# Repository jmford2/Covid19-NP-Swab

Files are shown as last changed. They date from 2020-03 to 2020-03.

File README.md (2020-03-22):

*Last updated: March 22, 2020 08:00 ET*

# Making NP swabs

As clinical laboratories around the world have begun testing for Covid-19, we have encountered a new crisis: a shortage of the swabs required to obtain the necessary sample. These are called nasopharyngeal swabs, or NP swabs for short.

**The goal of this repository is sharing [methods](#design), [testing procedures](#testing), and [results](#results) required to manufacture NP swabs locally/everywhere at volumes of thousands per day, until standard manufacturers can make and deliver more.**

Because the crisis is **now,** the goal is to re-create versions of the swabs already in use (as opposed to creating better/fundamentally different redesigns).

The files in this repo contain some information to get started. **This includes .stl files that you can modify/print (see [design_files](design_files/) above).**

If anyone has any questions, please reach out to any of the contributors here or to Dr. Ramy Arnaout, MD, DPhil, at rarnaout@bidmc.harvard.edu.

Anything you find here is free for use for all.

### High-level summary, March 21:

We are pursuing three main approaches:
- 3D printing [shafts](#design) and [gluing](#adhesive) [flock](#flock). We have good shaft designs modeled on the images below. Bottlenecks (1) [finding](#adhesive)/[testing](#testing) PCR-compatible glues. (2) High-throughput assembly and packaging. [Results](#results) should start appearing below.

- 3D printing all-in-one swab (meaning printing bristles together with/on shaft). We have promising designs (something like the below; stl/CAD files coming) but need to iterate to get to something usable; bottleneck is materials testing.

- Repurposing existing swabs. We are testing materials.

We will report results as we have them below.

If you want us to test swab materials at BIDMC we are happy to, you can **overnight** them to **Dr. Ramy Arnaout, MD DPhil, 508 Heath Street #2, Chestnut Hill, MA 02467** (note we are setting up dedicated 24/7 receiving at the hospital so this address will change, but your material will still get here). 

For efficiency, we strongly suggest you find local partners either in addition or instead for [testing](#testing) and ask one of [us](#contact) for write access to share your [results](#results) here on the repo.

## Contents

- [Basic description of an NP swab](#design)
- [Requirements](#reqs)
- [Anti-requirements: What's not required](#not-reqs)
- [List of known acceptable swabs](#acceptable-swabs)
- [Manufacturing approaches](#approaches)
- [Flock](#flock)
- [Materials and adhesives](#adhesive)
- [Packaging](#packaging)
- [Testing procedures](#testing)
- [Results](#results)
- [Contact](#contact)

## Basic description of an NP swab

(Click images for larger versions)

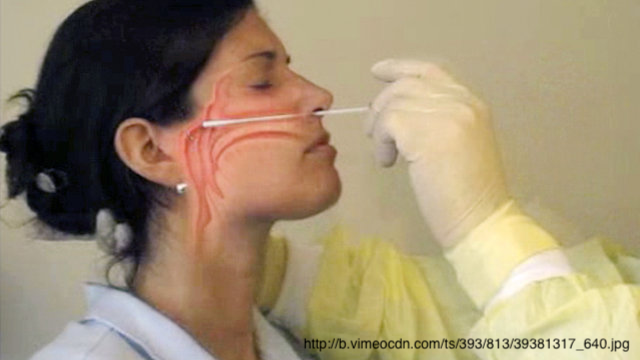
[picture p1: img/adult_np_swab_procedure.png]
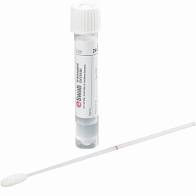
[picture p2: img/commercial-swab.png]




An NP swab is a flexible stick around 15cm in length that goes up your nose to the back of the nasal cavity (see [movie](https://www.youtube.com/watch?v=hXohAo1d6tk&feature=youtu.be&t=40)). It is swept or twirled around to brush or wick up secretions, which carry Covid-19 virus particles. The swab comes out of the nose and goes into a vial that contains fluid ([viral transport medium, VTM](Other_Docs/VTM_IU_recipe.pdf)). The vial gets capped and sent for processing.

There are **two parts**: a bristled **bulb** end (above) and a **shaft**. The bristles in the above are nylon.

The bulb looks like it would be fluffy to the touch but it is not: the bristles are short enough that it feels more like hard foam.

Often the shaft itself has a thin **neck**, for flexibility, and a thicker **handle**. The handle is often **scored**---a weak point in the shaft---where you can break it off so the bristled part stays in the vial; the handle is then thrown away.

**Score at \~7 cm from bulb tip.** The location of the score (distance from the bulb along the handle) must be smaller than the height of the vial you use. For example, for the vials for use with Copan 480C swabs, the breakpoint is 7cm; for [15-](https://www.fishersci.com/shop/products/falcon-15ml-conical-centrifuge-tubes-5/p-193301) or [50-mL](https://www.fishersci.com/shop/products/falcon-50ml-conical-centrifuge-tubes-2/p-193321) conical tubes (of the kind used routinely in biomedical research and sold by many manufacturers), 11 cm will do. It is mildly easier for handling if the score is close to the height of the vial but the requirement is that it is less than the height.

Helpful target measurements:

- Diameter of head with bristles: 3mm
- Diameter of head without bristles: \~2mm
- Diameter of neck: 1mm
- Diameter of handle: 2.5mm
- Length of bulb: 15mm
- Length that will be submerged in [transport medium](#pcr): \~30mm

# Requirements

## Medical requirements

-	**Stiffness, flexibility.** Wand is stiff enough to push to the back of the nasal cavity but flexible enough to get up the nose and will bend when it hits resistance instead of stabbing people (for reference, swabs are a little more flexible than the tiny straws used for coffee, and somewhat similar to the inside tube that holds the ink when you take apart a Bic ballpoint pen). **Swab must not snap off in patient's nose**

-	**Tip.** Ideally, the bulb end is *flocked* (see below): it has lots of tiny bristles perpendicular to the wand (see close-up above). The bristles provide for a high surface-area-to-volume and helps both wick secretions onto the bristle and liberate particles when put in the transport medium. Perpendicularity is a nice-to-have that we believe may improve yield slightly but requires electrostatic deposition; even random orientation of flock should work fine

-	Bristles or collecting substrate (including any adhesive) must be firmly attached and not get left behind in the nasal cavity. Similarly no part of the swab should break off or get left in the nasal cavity

-	[Materials](#adhesive) cannot inhibit [PCR](https://en.wikipedia.org/wiki/Reverse_transcription_polymerase_chain_reaction). This means no wood or cotton (although we believe rayon is OK). Nylon and polypropylene seem to be good choices, but start with medical equipment/grade materials if possible since they should be high quality/pure (some additives can be inihibitors).

-	Wand must break off inside the tube – better to be too short than too long.  Wand could be manually scored to create a weak point. If not, might need scissors at point of care (not ideal)

For more technical requirements, see [Design Constraints](Other_Docs/Design%20Constraints.md)

## Anti-requirements: What's not required

-	Sterility. Not a major concern for most uses; only for immunocompromised (in which case the ability to decontaminate by [autoclaving](https://en.wikipedia.org/wiki/Autoclave) or ethanol or isopropanol bath is needed). The air and the nose are already non-sterile and the PCR assay is specific enough to ignore most contaminants (as long as other Covid-19 contaminated things/people don’t come in contact with it and it doesn’t pick up PCR inhibitors)

-	Labor intensive is ok, to fill short term needs. There are students and researchers out of school and lab who are willing to volunteer to hand-assemble these from inoculation loops, adhesive, and wicking substrate #studentArmy

## List of known acceptable swabs

Model what you make after one of these.

Product numbers are listed. Unless otherwise stated, these are from the [FDA approved list](https://www.fda.gov/medical-devices/emergency-situations-medical-devices/faqs-diagnostic-testing-sars-cov-2) current as of **March 20, 2020**. You can look these up online.

**Copan:** 480C *(2)*, 481C *(1)*, 482C *(1)*, 501CS01, 503CS01, 516CS01, 518CS01, 534CS01

**Puritan:** LA-117 *(1)*, 3317-H, 25-3317-H, 25-3316-U, 25-3316-H, 25-3317-U, 25-3318-U, 25-3318-H, 25-3319-H, 25-3320-U, 25-3320-U EMB 100MM, 25-3320-U EMB 80MM, 25-3320-H and 25-3320-H EMB 80MM

*(1)* Preferred, per FDA

*(2)* Acceptable, per BIDMC

## Manufacturing approaches

**We believe the best use of resources is to be creative around copying the template, not redesigning swabs.**

- 3D print a shaft, and attaching flock material via adhesive

- 3D print a shaft with enough definition---either "nubs" along the surface or bristles---to gather secretion from the nasopharynx.

For more detail on ideas not yet investigated, including repurposing unrelated items like cosmetics applicators, or using other items common in labs, see [Other Approaches](Other_Docs/Repurposing_Approach.md)

### 3D-print shaft + adhesive + swab

- 3D print a wand with the appropriate form factor (e.g. see the picture above and the .stl files)
- dip bulb in adhesive (we are working on appropriate adhesives)
- dip sticky bulb in [flock](#flock)
- shake/blow/rinse off excess flock
- (if needed) dip in 70% ethanol for sterilization

(This is like how you'd solve this problem if you were in elementary school.) Currently we have no proven way to automate the last three steps so we are envisioning a "student army." Better ideas welcome.

### 3D-print entire swab

The ability to print a swab complete with bristles or equivalent saves the steps for requiring adhesive and [flock](#flock). 

Stereolithography 3D printed prototypes by **OPT Industries** look promising (see example bulbs, below---note in this approach the whole swab including bulb is printed at once, on their own DLP/SLA machines); we are testing materials now.
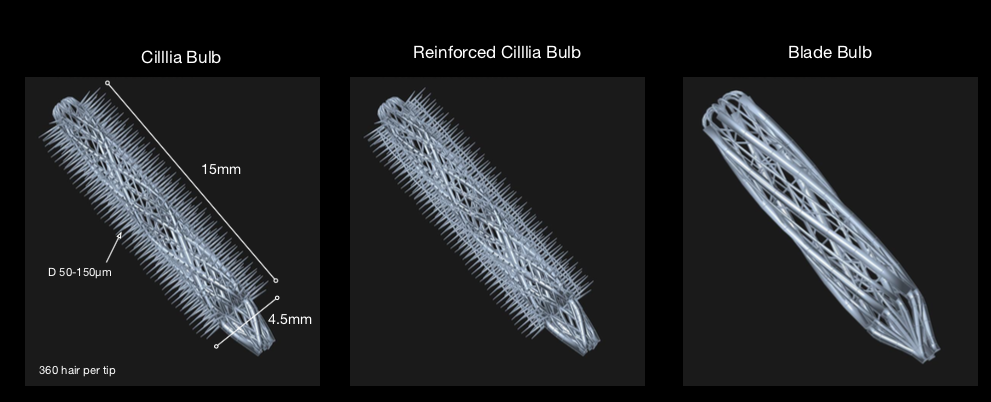
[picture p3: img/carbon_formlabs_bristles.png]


## Flock

"Flock" is the name of the bristle material. It can be ordered from e.g. www.flockit.com as a powder. The below information comes from extremely helpful conversations with them and Celluseude, the manufacturer.

- The nylon flock on the tip of the picture is 3 [denier](https://en.wikipedia.org/wiki/Units_of_textile_measurement#Denier) (3 [dtex](https://en.wikipedia.org/wiki/Units_of_textile_measurement#Denier))

- The flock on the flocked swab above was likely applied using electrostatic deposition: flock coated with something positively charged, shaft coated with adhesive and electrically grounded. We do not need to do this: the previous version of swabs, still widely in use, have matted flock and they work well enough (slightly lower sensitivity but clinically for now we'll take it)

- In general acrylic is used as the adhesive for flock, but be aware that acrylic is a **known PCR inhibitor** (see below). Decision point is rinse a lot to remove loose acrylic vs. just use something safer. Apparently Elmer's has something of the same problem.

- The only colors you should consider for the nylon are black and white, with preference for white. Black has some inorganic compound that is assumed to be PCR-safe; white has titanium inside the fiber but not on the surface so is more likely PCR safe. (White is the purest nylon.) Colored nylons have various ionic or covalent groups on the outside, which are unnecessary complications.

- Rayon is also safe to use

## Shaft

This is the easiest part to 3D-print.

It should be able to be easily broken off, so that only the tip with the patient's nasal secretion is in a specimen container.  Easy break-off may be accomplished via scoring.

## Packaging

As we get closer to having swabs, we will want a solution for packaging. Ideally at least semi-sterile, definitely single-swab packaging.

Possibly will want to fork this process: more sterile for immunocompromised patients, less for others.

Current best thought is to package manually in sterile hoods:

- begin with swabs in ethanol vat/bucket
- spread and cut plastic wrap
- leave under UV light in hood (*1*)
- take swab out of ethanol and place horizontally on strip of plastic to dry
- **When dry,** fold plastic over swab
- packing done

(*1*) UV is not expected to destroy plastic on timescales of under a few hours

Thoughts on throughputting this?

## Materials and adhesives

Adhesives will need to adhere the two substances (printed shaft + flock) and will need to not leave behind anything in the nasal cavity / nasopharynx when used.

Some materials and adhesives inhibit PCR (see [testing protocol](#pcr) below). See the [Kodzius 2012](Other_Docs/kodzius2012.pdf) and [forensicGEM's work](Other_Docs/forensicGEM_Tissue_AppNote_TapeInhibition.pdf) for details.

From those files:

### Safe materials (any red bar above \~50 in [Kodzius Fig. 3](Other_Docs/kodzius2012.pdf)): (*1*)
- polypropylene
- PTFE
- PDMS
- SiO2 quartz
- Pyrex glass
- Soda-lime glass
- NOA68

### Unsafe materials:
- PMMA
- Silicon
- SiO2 5600A
- ITO glass
- SU-8
- NOA61

### Unknown:
- metals including steel and aluminum (in principle these stick to polymerase, but the effect size depends on the form factor so we don't know yet)
- polycryl resin (we believe the monomers are not PCR safe, but if cured and washed could be ok; we will test)

### Safe adhesives (from Kodzius Fig. 3 and from forensicGEM document Fig. 1):
- Wax (Tm 80C)
- the glue used in Scotch Magic Tape 810
- the glue used in Scotch Crystal Clear Tape
- the glue used in Scotch Mailing Tape
- the glue used in Scotch Storage Freezer Tape
- the glue used in Scotch Transparent Tape 550
- the glue used in Sellotape Brown Packaging Tape
- the glue used in Applied Biosystems MicroSeal Adhesive Film

### Unsafe adhesives:
- Wax (Tm <80C)
- Epoxy glue
- Acrylic glue
- the glue used in Scotch Masking Tape (made in Canada or Taiwan)
- the glue used in Scotch Removable Magic Tape 811
- the glue used in Sellotape Diamond Ultra Clear
- the glue used in Sellotape Invisible Permanent Write-on
- the glue used in Sellotape Cellulose Easy-Tear Tape
- the glue used in Sellotape Double-Sided Tape
- the glue used in 3M PostIt notes

(*1*) Some materials can in principle be used as adhesives, e.g. PDMS

## Testing procedures

We propose/are using a three-step testing procedure:

- expert review
- sufficient collection of material
- PCR compatibility

### Expert review

There is no substitute for having a health professional who actively uses NP swabs evaluate your prototype. If such an expert says it "looks good," that is enough to pass this test (see [Results](#results) below)

Two frequently-asked questions are re: length and flexibility. For length, our current recommendation is 15cm. For flexibility: if you have a [swab to compare to](#acceptable-swabs), that is the best way to guage flexibility. If not: your swab should as flexible as the inside part of a standard Bic ball-point pen (the tube that contains the actual ink, when you take the pen apart).

### Sufficient collection of material

For collection of material:

- swirl against the inside of your cheek (make sure the swab is clean first)
- rub on a slide
- perform a [Gram stain](https://en.wikipedia.org/wiki/Gram_stain)
- visualize under a microscope
- take picture through ocular
- compare picture to control we made using an actual NP swab (to be posted soon)

The viral particles we are looking to collect are smaller than bacteria, but if you collect a fair number of bacteria, that is considered Ok for now (ask a microbiologist or microbiology tech, and we will provide a picture of what we think is acceptable when we can).

### PCR compatibility

It is essential to confirm that nothing in the final product (material ± adhesive) inhibits RT-PCR, on which current tests are based (details of the reagents differ somewhat from assay to assay; we will post). A testing protocol is as follows. Note because this has a substantial incubation time, **it is a good idea to start testing materials before prototypes are done, if possible.**

- incubate bulb in 3mL Viral Transport Medium (VTM; [recipe courtesy IU](Other_Docs/VTM_IU_recipe.pdf)) overnight (12 hr)
- spike the VTM with positive control (*1*)
- aliquot 700µl for testing
- run RT-PCR (*2*) (*3*)

(*1*) If you are working with clinical labs who have the bandwidth, they can use inactivated Covid-19 particles that are used clinically as the positive control any virus. If not, and you are/have access to colleagues in a virology lab working with encapsulated virus, that can be used. If not, then any mRNA.

(*2*) Many protocols and reagents are proprietary, but many hospitals have developed their own laboratory-developed tests (LDTs) that may have made their protocols publicly available. If you find and [forward](#contact) we will post.

(*3*) An RNA extraction step [may not be required](https://www.biorxiv.org/content/10.1101/2020.03.20.001008v1)

See also [this FDA page](https://www.fda.gov/medical-devices/emergency-situations-medical-devices/faqs-diagnostic-testing-sars-cov-2) for speific testing details.

## Results

As materials and designs (including existing swabs) get tested, we will record results here. Please organize entries into the following fields. We plan to turn into a (sortable) table, but don't wait for that: just upload entries (separating each entry by line breaks). Please **copy** the below for each entry (i.e., don't overwrite it). If you need help [contact us](#contact).

___

### ENTRY TEMPLATE

#### Identifier
This is a unique identifier, ideally including the source's name

#### Date of test

#### Test site
E.g., BIDMC

#### Picture
Please take a high-resolution picture of the **entire** item provided.

#### Material
Please describe all (known) materials in the bulb head, including plastic, any adhesive, and any flock

#### Process
Please include a brief description of the design process that an expert would understand well enough to reproduce. For repurposed swabs, write "commercial."

#### Creator (contact info and company)
How to contact the creator for questions/further development

#### Link to stl and cad files
Please send .stl and CAD files, which we will post.

#### Test 1: NP swab user evaluation (eg an ID doc), with comments
If passes, write "Pass". If fails, write "Fail" and give a brief reason why. Should be filled out by someone who has experience actually using NP swabs in a clinical context. Please leave the name of this person.

#### Test 2: Collection test
If a Gram stain of the (inner) cheek made from the swab shows material broadly consistent with our control, then write "Pass". If not, "Fail" and give reason (too abrasive, did not pick up material, etc.)

#### Test 3: PCR compatibility (and which protocol used)
As above, "Pass" vs. "Fail". Please indicate the protocol used. You can post the protocol in the Testing/ directory, and link to it here

___

## Contact us

We want to emphasize this is a **group effort** with literally scores of people working on this right now; if you're reading this, you're probably one of them. If you have something to contribute, please contact Dr. Ramy Arnaout, MD, DPhil, at rarnaout@bidmc.harvard.edu.

Note there's also now a [Slack channel](https://join.slack.com/t/rapidmanufact-iop4498/shared_invite/zt-cykndes6-XtxzG~8bkji64M3wTVWiOw).

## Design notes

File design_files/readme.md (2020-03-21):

# Please upload and download models here

## Abiogenix Models
- Goutam Reddy (greddy@abiogenix.com)
- Fusion 360 links to CAD models

1) nasopharyngeal swab nubs V1:  https://a360.co/2Qyh2GE
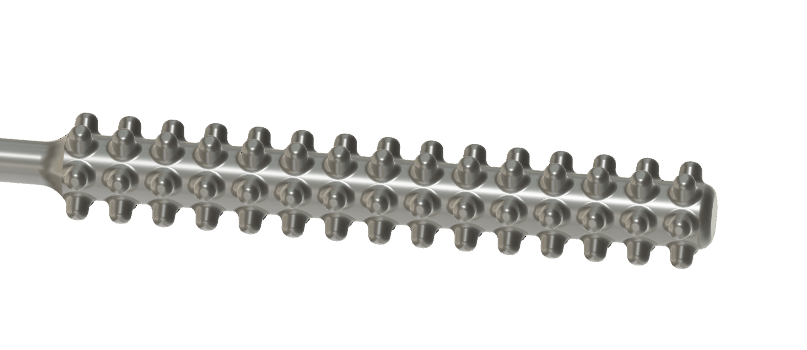
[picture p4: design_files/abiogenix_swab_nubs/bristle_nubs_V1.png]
   - 
   - bristle with 6x15 0.7mm dia raised nubs,
   - bristle surface area 129 mm^2
   - need to fix shaft so max-stress point is at snap-off point, not on bristle shaft
    
2) nasopharyngeal swab round V1:  https://a360.co/2wpGHui
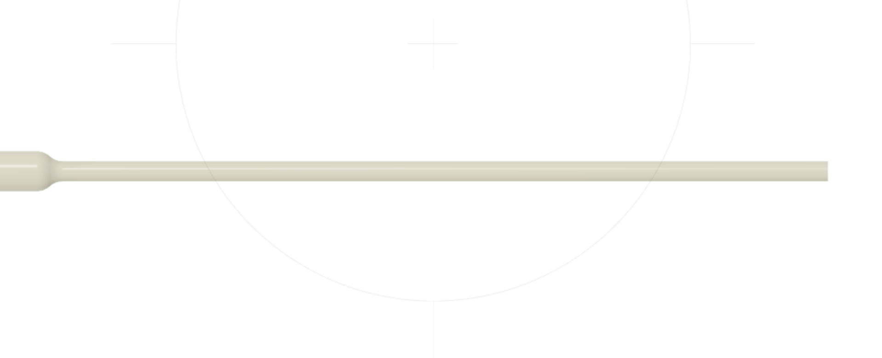
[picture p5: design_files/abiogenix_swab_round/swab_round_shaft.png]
   - 
   - featureless bristle: 1.25mm diameter shaft
   - bristle surface area: 61 mm^2
   - LESS SURFACE AREA BUT CAN BE USED TO ATTACH EXTERNAL BRISTLE OR COATING
   
3) nasopharyngeal swab nubs holes V1: https://a360.co/2U5CzbK
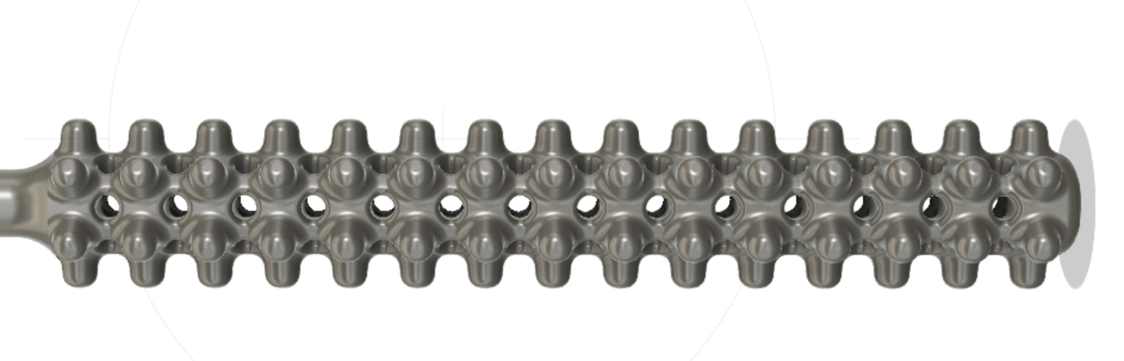
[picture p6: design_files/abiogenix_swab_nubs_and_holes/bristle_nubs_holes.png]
   - 
   - bristle with 6x15 0.7mm dia raised nubs, and 0.35mm dia holes
   - bristle surface area: 167 mm^2
   - PREFER NOT TO USE MODELS WITH HOLES INSIDE TO REDUCE POST-PROCESSING

## Wyss Institute Models
- *find author contact info*
- *find link to original model files*
1) nasopharyngeal swab helix: *find link to model*
2) nasopharyngeal swab linear balls: *find link to model*



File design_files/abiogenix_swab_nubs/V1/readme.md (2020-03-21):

These swabs were modeled in Autodesk Fusion 360
- available here: https://a360.co/2Qyh2GE


# Nubs Surface Area
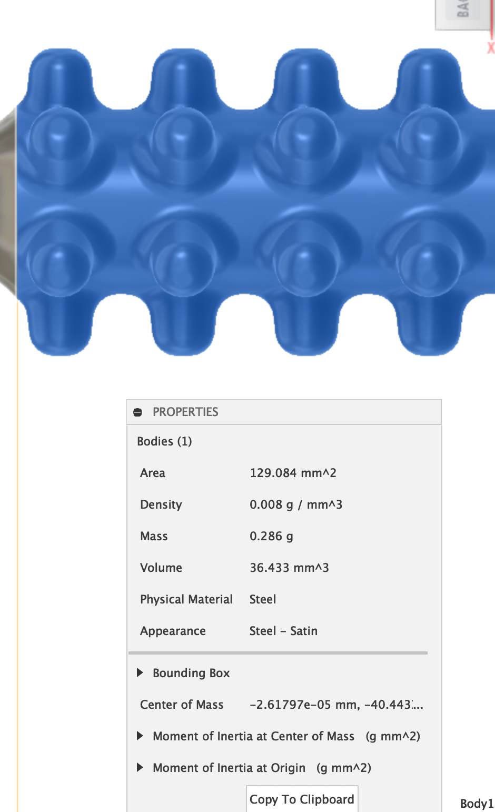
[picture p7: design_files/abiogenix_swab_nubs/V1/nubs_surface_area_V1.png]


# Nubs Break Point
- shaft snapped off at head of bristle
- TODO: weaken break-point area and strengthen briste-shaft interface 
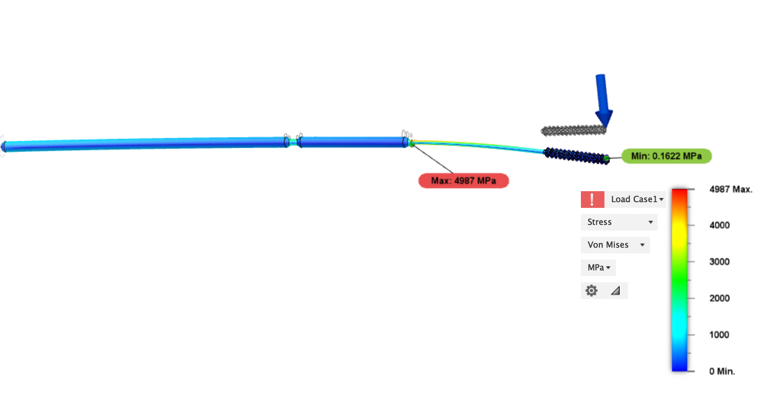
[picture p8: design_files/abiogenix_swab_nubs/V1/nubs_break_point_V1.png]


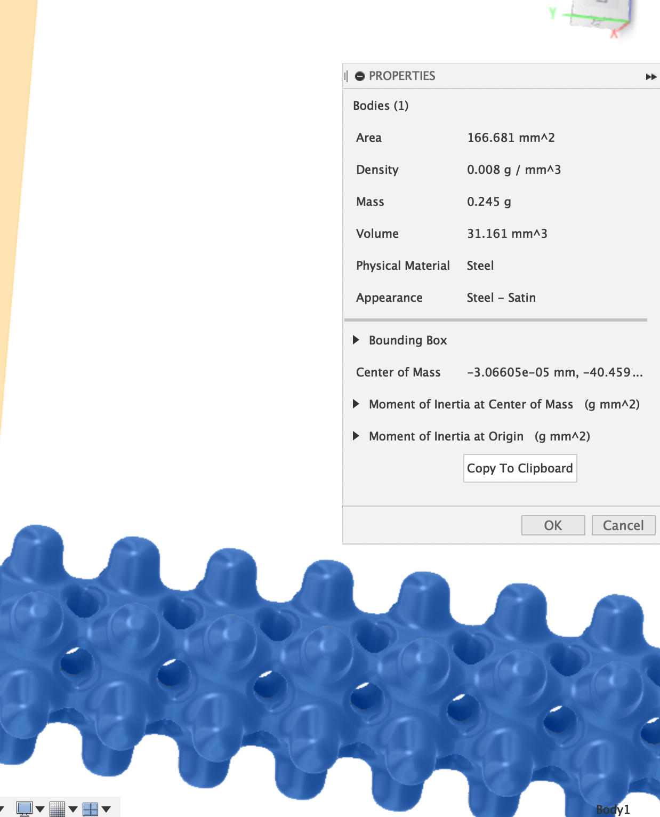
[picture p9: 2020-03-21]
design_files/abiogenix_swab_nubs_and_holes/nubs_holes_surface_area_v1.png

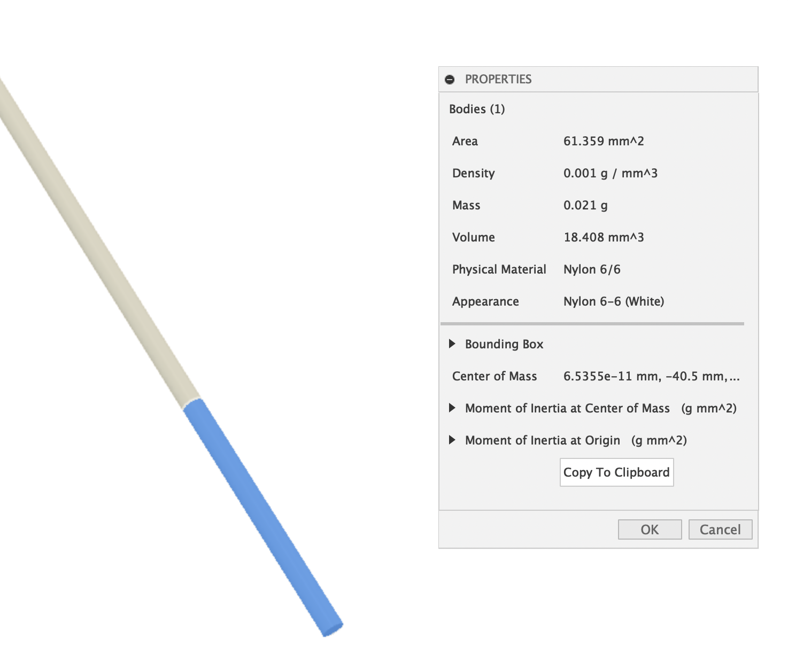
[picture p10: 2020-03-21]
design_files/abiogenix_swab_round/round_surface_area_V1.png

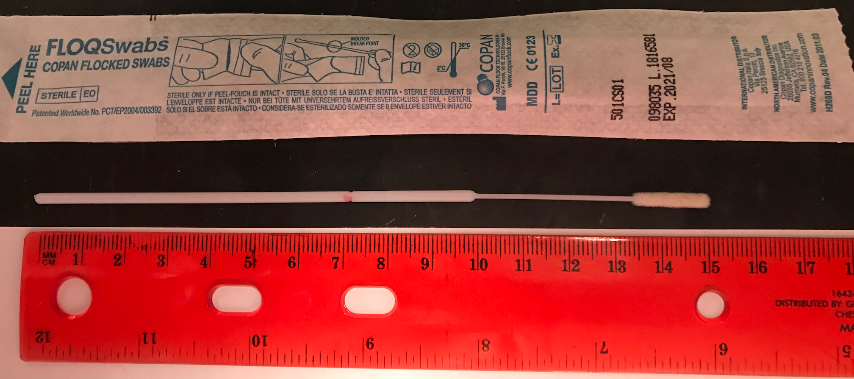
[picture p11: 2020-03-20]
img/copan_flocked_swab_macro_lores.png

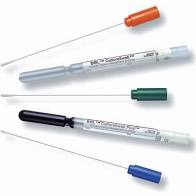
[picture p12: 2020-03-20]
img/commercial-swabs.png

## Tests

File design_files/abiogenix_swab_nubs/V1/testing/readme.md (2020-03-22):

These swabs were printed using HP MJF 3D printing technology using PA12 material at Fathom Studios in Oakland Ca.

# Flexibility
- swabs are quite flexible
- can bend more than 180 degrees without breaking
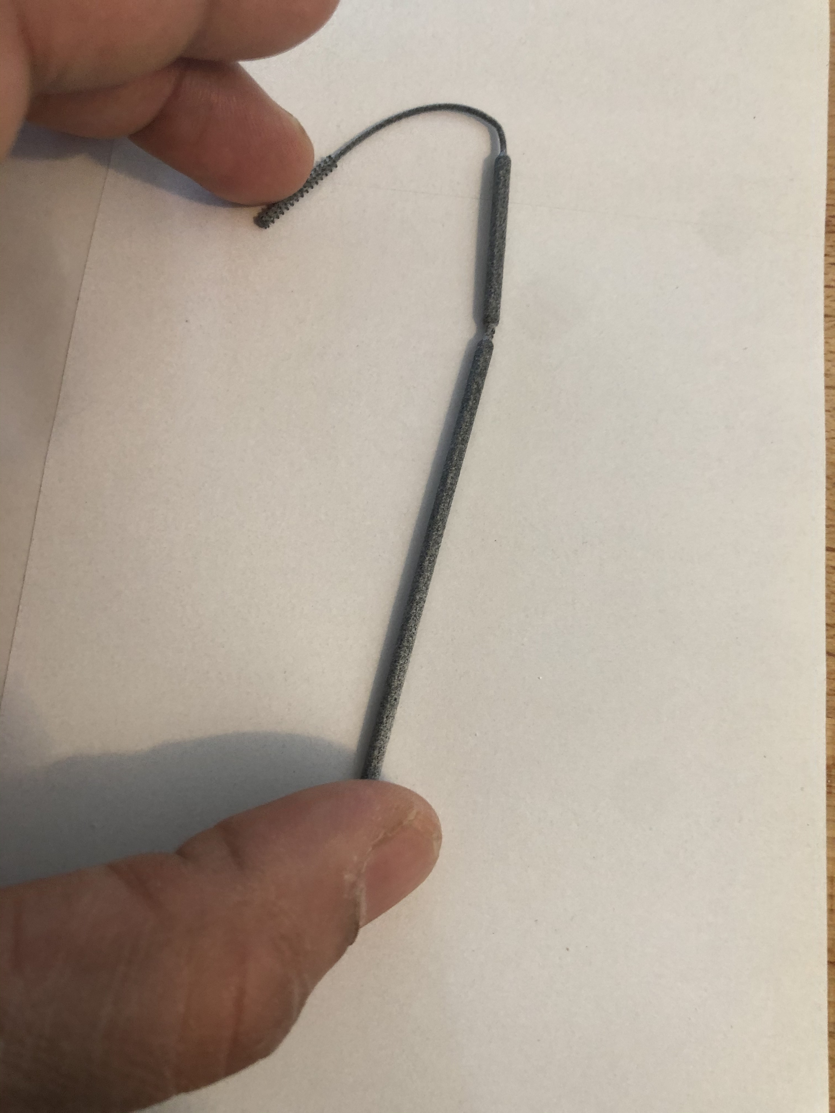
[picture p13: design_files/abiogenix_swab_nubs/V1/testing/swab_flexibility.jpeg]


# Torsional Load (twisting)
- ISSUE: shaft snapped off at head or along body of bristle with 540 degrees of twisting (tested on 3 - 540, 720, 900 degrees)
- TODO: define spec for torsional load, add tests in simulation, strengthen bristle to shaft interface to ensure breakage at snap-point
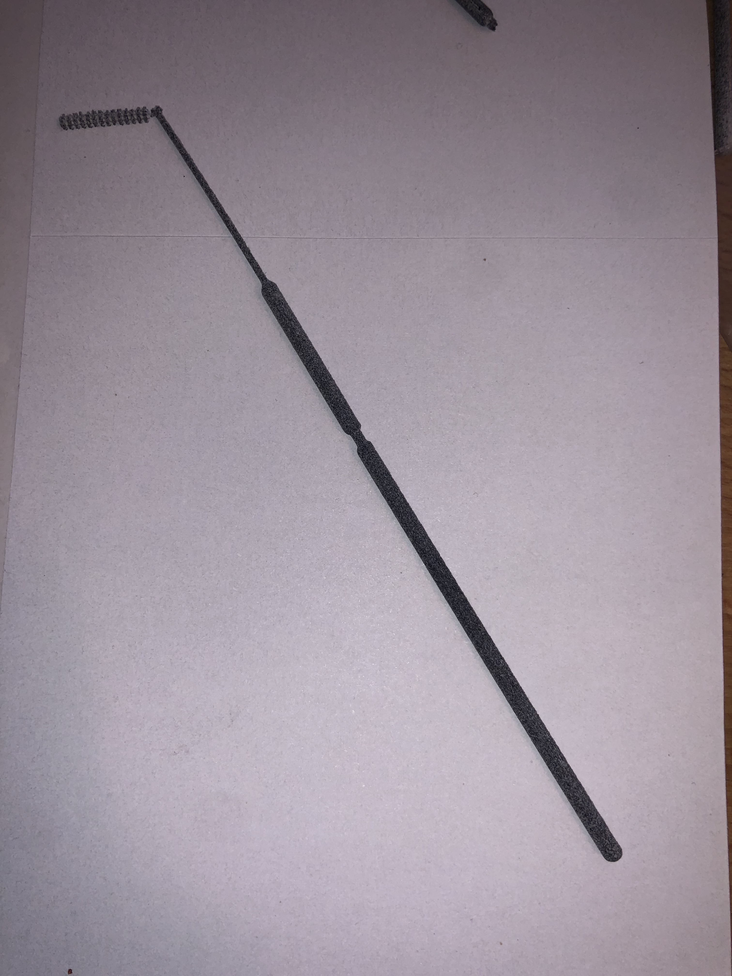
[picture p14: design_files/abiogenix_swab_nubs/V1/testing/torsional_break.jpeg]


# Static Load at Tip (bending to break)
- ISSUE: bends first and eventually breaks at bristle to swab shaft interface
- ISSUE: break-off-point requires multiple back-and-forths bendings to break off
- TODO: make break-off-point weaker (test V's, grooves, stress points - in simulation)
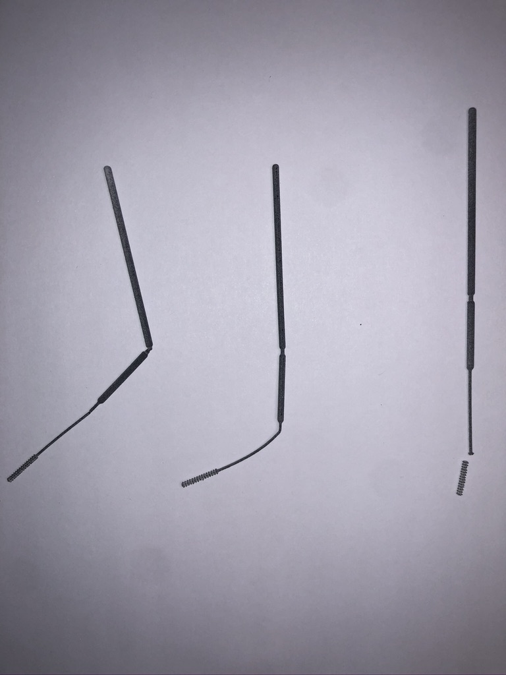
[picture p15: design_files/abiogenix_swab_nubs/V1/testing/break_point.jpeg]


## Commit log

2020-03-20 Add files via upload
    no nubs- just a flat end - 1.25 dia bristle diameter
    [nasopharyngeal swab flat V1.stl]
2020-03-20 adding Materials list
2020-03-21 README
    adhesives, materials, sterilization
2020-03-21 Carbon, Formlabs' prototypes
2020-03-21 Test materials early
